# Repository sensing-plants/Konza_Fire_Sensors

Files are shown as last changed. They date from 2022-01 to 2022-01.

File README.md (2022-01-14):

# Konza_Fire_Sensors
These sensors will be used to monitor the temperature of a grassland fire using K-type thermocouples, Adafruit Adalogger, Adafruit ds3231 Featherwing, and MCP9600 i2c thermocouple amplifier.

The sensors will be inclosed in a fire resistant box or PCV pipe to protect it from the fire. Temperature within the enclosure will be monitored by both the MCP9600 cold junction and the ds3231 temperature sensor.

A red light will flash if the data was properly recorded on the SD card.

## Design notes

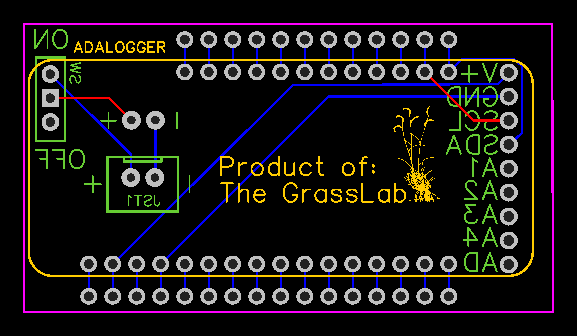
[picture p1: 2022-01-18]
PCB Schematics/PCB_Konza_Fire_2022-01-17.png

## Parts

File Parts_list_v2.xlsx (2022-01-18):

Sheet: Adalogger
Product | Price | Bulk Price | Link | Purpose | Comments | Item | price | shipping | units | Unit price | Product | Price | Bulk Price | Link | Purpose | Comments
Adalogger | $19.95 | $17.96 | https://www.adafruit.com/product/2796 | microcontroller with sd module |  | PCBs | $20.00 | $30.00 | $50.00 | $1.00 | AD8495 | $11.95 | $10.76 | https://www.adafruit.com/product/1778 | k-type thermocouple amplifier | alternate part for MCP9600
DS3231 | $13.95 | $12.56 | https://www.adafruit.com/product/3028 | date/time | If you just want time in seconds, we can leave this off
CR1220 | $0.95 | $0.86 | https://www.adafruit.com/product/380
SD card | $4.95 | $4.46 | https://www.adafruit.com/product/5252 | data storage | 8GB or smaller
MCP9600 | $15.95 | $14.36 | https://www.adafruit.com/product/4101 | universal thermocouple amplifier
thermocouple wire | $0.00 | $0.00 |  | measure temperature | we have some from our lab that we can use
batteries | $14.95 | $13.46 | https://www.adafruit.com/product/328 | power | these could be swapped for AA or AAA batteries
switch | $0.95 | $0.86 | https://www.adafruit.com/product/805 | turn on/off
fireproof housing |  |  |  | protect electronics | Hopefully the ones you have will work
femal headers | $0.95 | $0.86 | https://www.adafruit.com/product/2886
stacking headers | $1.25 | $1.13 | https://www.adafruit.com/product/2830
PCB | $1.00 | $1.00 |  | connecting electronic components | I have designed these and can have them manufactured and delivered in about 1-2 weeks
Total | $74.85 | $67.51

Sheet: Boron
Product | Price | Bulk Price | Link | Purpose | Comments
Particle Boron LTE | $67.21 |  | https://store.particle.io/collections/gen-3/products/copy-of-boron-lte-cat-m1-noram-starter-kit | microcontroller w LTE and IoT
AD8495 | $11.95 |  | https://www.adafruit.com/product/1778 | k-type thermocouple amplifier
type K thermocouple wire |  |  | https://www.adafruit.com/product/270 |  | this is for 1 m…we can get bulk wire for cheaper and could cut it to whatever length we want
batteries | $14.95 |  | https://www.adafruit.com/product/328 | power
switch | $0.95 |  | https://www.adafruit.com/product/805 | turn on/off
IoT platform | $0.00 |  |  | data storage/visualization/diagnostics
cell service | $0.00 |  |  | data transfer
 | $95.06

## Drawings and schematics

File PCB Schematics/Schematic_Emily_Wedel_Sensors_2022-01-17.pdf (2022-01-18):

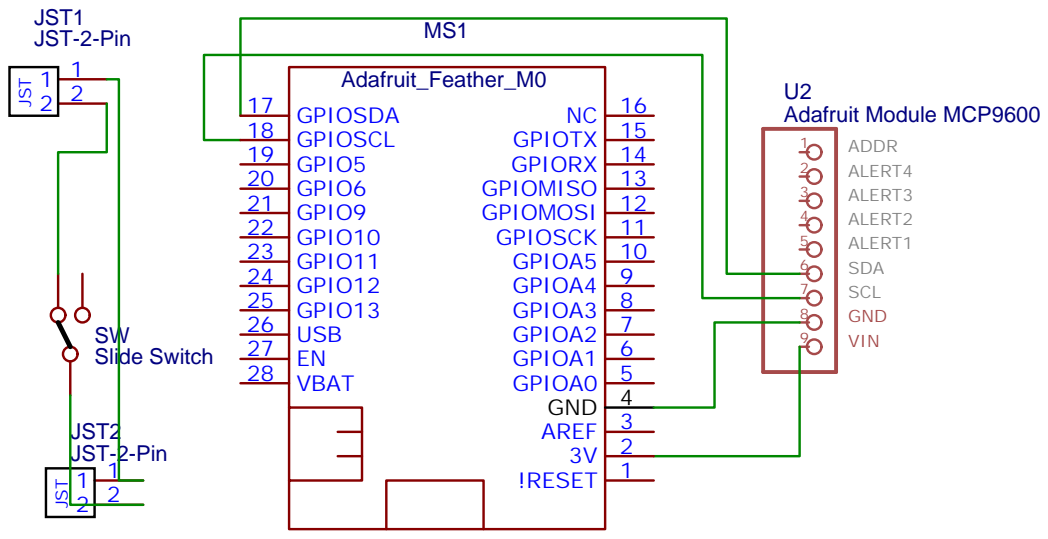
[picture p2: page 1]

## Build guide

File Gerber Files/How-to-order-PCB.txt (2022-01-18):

How to Order PCB

Please refer to:
https://docs.easyeda.com/en/PCB/Order-PCB

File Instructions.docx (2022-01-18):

# Installing the Arduino IDE:

1. Follow instructions from Adafruit about installing the IDE (https://learn.adafruit.com/adafruit-feather-m0-adalogger/setup) and setting it up to support their boards (https://learn.adafruit.com/adafruit-feather-m0-adalogger/using-with-arduino-ide).
2. You will also need to install the RTClib and Adafruit MCP9600 libraries for this sketch to load properly from your computer/tablet.
  a. Go to Sketch → Include Library → Manage Libraries…
  b. Type “MCP9600” in the search bar and find the library by Adafruit
  c. Clear the search bar and type “rtcLib” and find the library by Adafruit

# Sensor Set-up:

1. Insert the microSD card
2. Insert the thermocouple into the screw terminal on the MCP9600 board
  a. If already inserted, check that the screws are tight and connection is secure
3. Open the Arduino IDE on a computer/tablet
4. Go to Tools → Board: → Adafruit SAMD (…) boards → Adafruit Feather M0
5. Connect the microcontroller to the computer
  a. Check for the established serial connection port
    i. Tools → Port → COM?(Adafruit Feather M0)
6. Open the Serial monitor to for diagnostics check
  a. Make sure the program is running
  b. Check that the time stamp from the computer is similar to the sensor
  c. Check the 3 temperatures provided
    i. they should be relatively close but the RTC and cold junction temps are usually a little higher due to the chip on the boards heating up
7. Place the sensor in side of the housing and secure the cap

# Quick check:

1. The red light should flicker a few times and then blink every second to indicate that the data is getting logged to the SD card
2. If the green light is on or flashing, see the trouble shooting section below.

# Trouble shooting:

1. If the temperature seems far off for the hot junction, check that the thermocouple wires are in the right location
  a. If you hold the thermocouple end in your hand and the temp goes down, the wires are backwards
2. If the green light is blinking it means there is no SD card inserted.
3. If the green light is on and not flashing, it means it could not initialize the SD card
  a. If it couldn’t initialize the SD card, clean the contacts of the SD card
    i. If it still doesn’t work, try a different SD card or format the current card
      1. Formatting the card will erase all data on the card so be sure to download it first!!!

# Battery Charging:

1. Remove the SD card
2. Turn on the board
3. Attach USB to 5V (1 Amp) power source
4. The Yellow/Orange light next to the Micro USB port will turn on if the battery is charging

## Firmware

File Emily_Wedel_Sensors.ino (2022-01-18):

/*
Sensors designed for Emily Wedel to measure temperature of fires in watersheds at Konza.

This set-up uses a adafruit Adalogger and ds3231 featherwing to log data and track time.
K-type thermocouple will be measured with a MCP9600 universal thermocouple amplifier that uses I2C communication.
This sketch also flashes a green light after data has been logged as an indicator that the data is being logged properly.
 */
/**************************************************
      define the pin for monitoring the battery
**************************************************/

#define VBATPIN A7

/**************************************************
      set time of sample interval
**************************************************/

unsigned int sample_interval = 1 * 1000;

/**************************************************
      RTC set-up
**************************************************/

#include "RTClib.h"
RTC_DS3231 rtc;

/**************************************************
      SD Card set-up 
**************************************************/

#include <SPI.h>
#include <SD.h>

const int chipSelect = 4;
int sd_pin = 7;
int grnLED = 8;
int redLED = 13;

/**************************************************
      Thermocouple amplifier set-up 
**************************************************/

#include <Wire.h>
#include <Adafruit_I2CDevice.h>
#include <Adafruit_I2CRegister.h>
#include "Adafruit_MCP9600.h"

#define I2C_ADDRESS (0x67)

Adafruit_MCP9600 mcp;

void setup()
{
    Serial.begin(115200);

    pinMode(sd_pin,INPUT);
    pinMode(grnLED,OUTPUT);
    pinMode(redLED,OUTPUT);
    digitalWrite(redLED,LOW);

/**************************************************
      RTC Initialization and set time
**************************************************/

    if (! rtc.begin()) {
    Serial.println("Couldn't find RTC");
    Serial.flush();
    while (1) delay(10);
  }

//    rtc.adjust(DateTime(F(__DATE__), F(__TIME__)));


/**************************************************
      MCP9600 Initilization and set parameters
**************************************************/

    Serial.println("MCP9600 HW test");

    /* Initialise the driver with I2C_ADDRESS and the default I2C bus. */
    if (! mcp.begin(I2C_ADDRESS)) {
        Serial.println("Sensor not found. Check wiring!");
       
    }

  Serial.println("Found MCP9600!");

  mcp.setADCresolution(MCP9600_ADCRESOLUTION_18);
  Serial.print("ADC resolution set to ");
  switch (mcp.getADCresolution()) {
    case MCP9600_ADCRESOLUTION_18:   Serial.print("18"); break;
    case MCP9600_ADCRESOLUTION_16:   Serial.print("16"); break;
    case MCP9600_ADCRESOLUTION_14:   Serial.print("14"); break;
    case MCP9600_ADCRESOLUTION_12:   Serial.print("12"); break;
  }
  Serial.println(" bits");

  mcp.setThermocoupleType(MCP9600_TYPE_K);
  Serial.print("Thermocouple type set to ");
  switch (mcp.getThermocoupleType()) {
    case MCP9600_TYPE_K:  Serial.print("K"); break;
    case MCP9600_TYPE_J:  Serial.print("J"); break;
    case MCP9600_TYPE_T:  Serial.print("T"); break;
    case MCP9600_TYPE_N:  Serial.print("N"); break;
    case MCP9600_TYPE_S:  Serial.print("S"); break;
    case MCP9600_TYPE_E:  Serial.print("E"); break;
    case MCP9600_TYPE_B:  Serial.print("B"); break;
    case MCP9600_TYPE_R:  Serial.print("R"); break;
  }

  Serial.println(" type");

  mcp.setFilterCoefficient(3);
  Serial.print("Filter coefficient value set to: ");
  Serial.println(mcp.getFilterCoefficient());

  mcp.enable(true);

  Serial.println(F("------------------------------"));

/**************************************************
      SD Card Initialization and print file headers
**************************************************/
  while(digitalRead(sd_pin) == 0){
    Serial.println("No SD Card Inserted!!!");
    digitalWrite(grnLED,HIGH);
    delay(500);
    digitalWrite(grnLED,LOW);
    delay(500);
  }
  Serial.print("Initializing SD card...");

  // see if the card is present and can be initialized:
  if (!SD.begin(chipSelect)) {
    Serial.println("Card failed, or not present");
    // don't do anything more:
    while (1);
  }
  Serial.println("card initialized.");
  digitalWrite(redLED,HIGH);
  delay(20);
  digitalWrite(redLED,LOW);
  

  File dataFile = SD.open("datalog.csv", FILE_WRITE);

  // if the file is available, write to it:
  if (dataFile) {
    dataFile.println("date, time, v_bat, rtc_temp, hot_j, cold_j, adc");
    dataFile.close();
    // print to the serial port too:
    Serial.println("date, time, v_bat, rtc_temp, hot_j, cold_j, adc");
      digitalWrite(redLED,HIGH);
      delay(20);
      digitalWrite(redLED,LOW);

  }

}

void loop()
{
  String timeString = "";
  String dataString = "";


/**************************************************
      RTC get time
**************************************************/

      DateTime now = rtc.now();

    
    timeString += now.month(), DEC;
    timeString += '/';
    timeString += now.day(), DEC;
    timeString += '/';    
    timeString += now.year(), DEC;
    timeString += ",";
    timeString += now.hour(), DEC;
    timeString += ':';
    timeString += now.minute(), DEC;
    timeString += ':';
    timeString += now.second(), DEC;
    timeString += ",";

/**************************************************
      get the battery voltage
**************************************************/

float vbat = analogRead(VBATPIN)*2*3.3/1024;
dataString += vbat; dataString += ",";

/**************************************************
      MCP9600 get temperature data 
**************************************************/

  dataString += rtc.getTemperature(); dataString += ",";
  dataString += mcp.readThermocouple(); dataString += ",";
  dataString += mcp.readAmbient(); dataString += ",";
  dataString += mcp.readADC() * 2;
  

/**************************************************
      SD Card print time and data
**************************************************/
  
File dataFile = SD.open("datalog.csv", FILE_WRITE);

  if (dataFile) {
    dataFile.print(timeString);
    dataFile.println(dataString);
    dataFile.close();
    // print to the serial port too:
    Serial.print(timeString);
    Serial.println(dataString);
      digitalWrite(redLED,HIGH);
      delay(20);
      digitalWrite(redLED,LOW);

  }
  // if the file isn't open, pop up an error:
  else {
    Serial.println("error opening datalog.csv");
  }


/**************************************************
      delay for time of sample interval
**************************************************/
 
  delay(sample_interval);
}

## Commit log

2022-01-18 Create PCB Schematics
2022-01-18 Update Emily_Wedel_Sensors.ino
    Updated the code to check if an sd card is inserted and blinks the green light and prints to serial monitor if card is not present. Also added measured battery voltage to the sketch.
